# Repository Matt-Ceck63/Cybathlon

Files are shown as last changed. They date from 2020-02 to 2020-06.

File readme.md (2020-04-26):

This repository contains:

- Main assembly in solidworks (Old version, newer version saved in step files made in Fusion 360)
- Step Files:
	- Arm Assembly
	- Manipulator Assembly
- Bill of materials
- STM32F303K8 microcontroller reference files
- C program for the microcontroller
- Whole Cybathlon team wheelchair assembly with mounted arm

Rendered Assembly:

Front Side

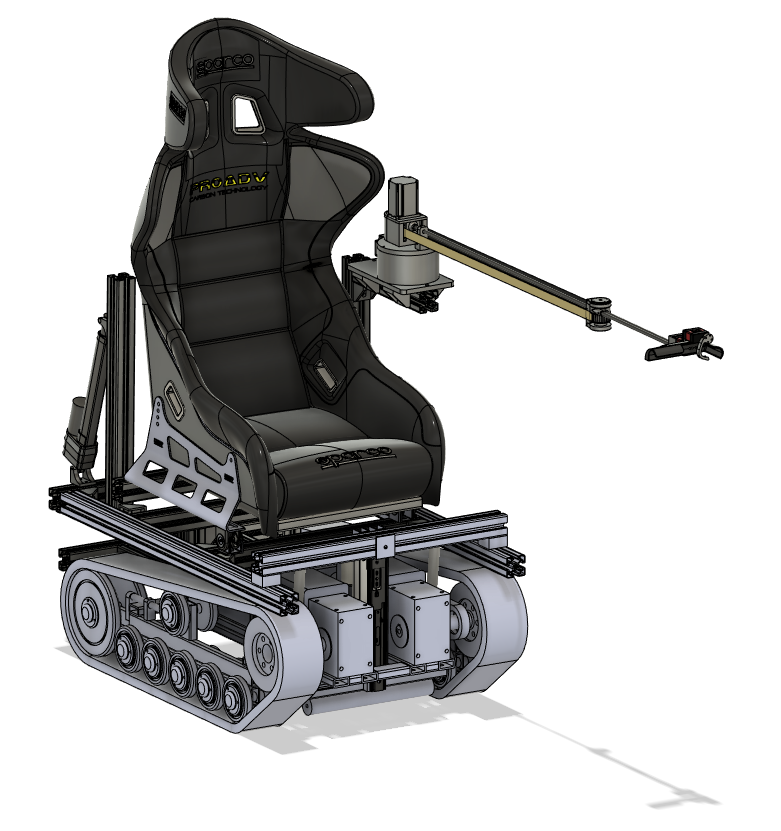
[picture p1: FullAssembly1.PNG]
Image Front Side


Back Side

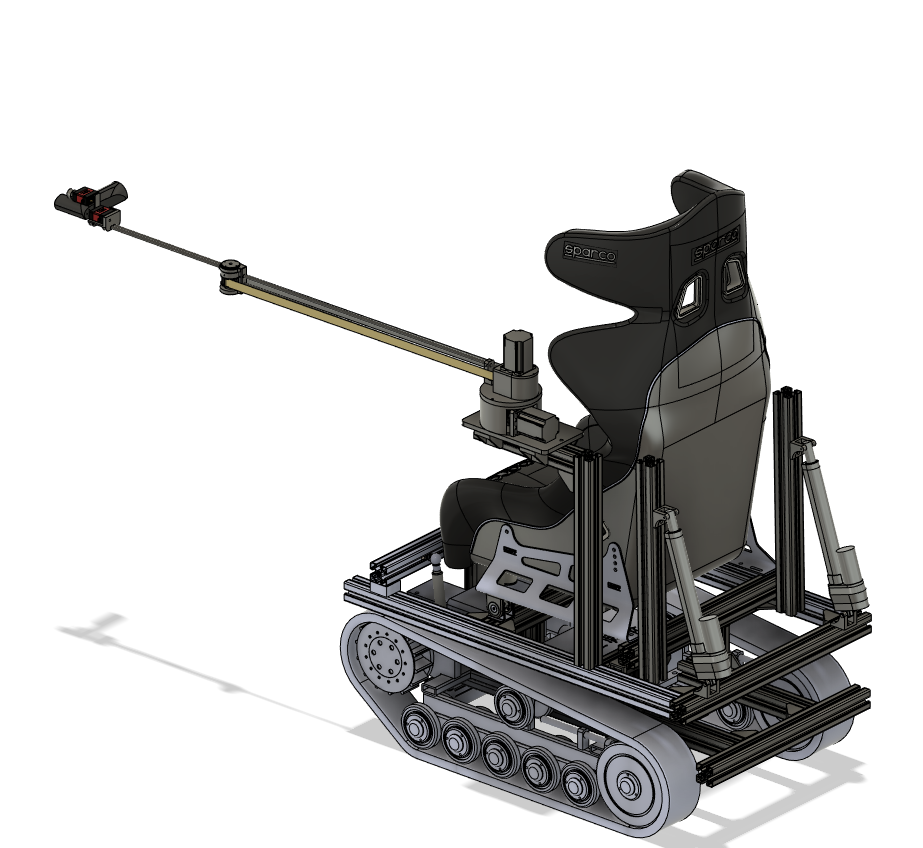
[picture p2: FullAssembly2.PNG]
Image Back Side


Top

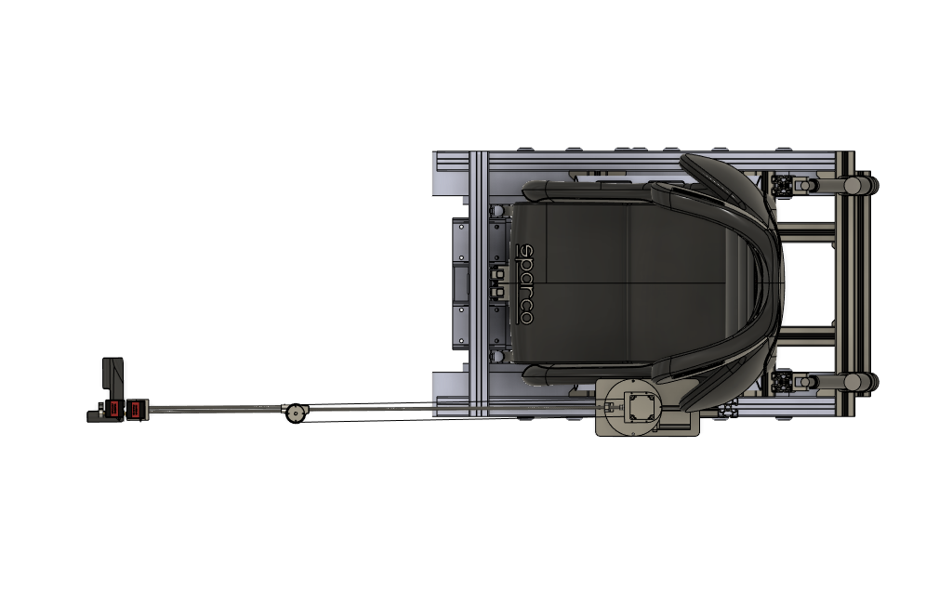
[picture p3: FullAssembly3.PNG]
Image Top


Front

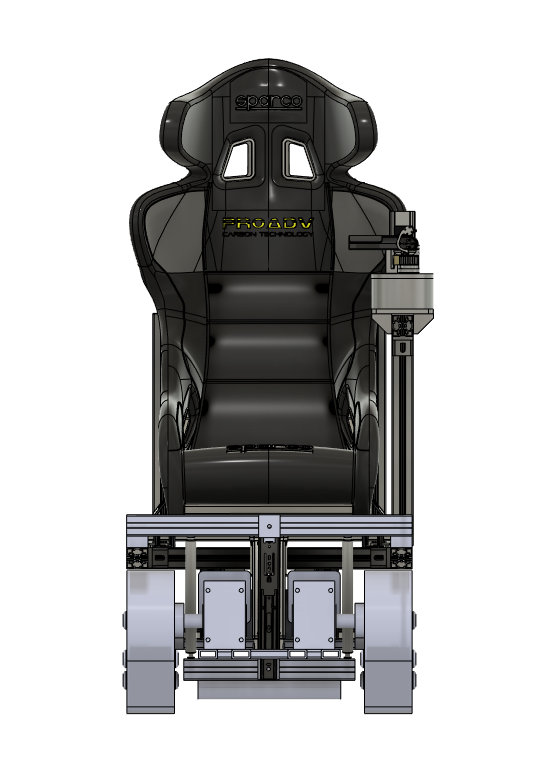
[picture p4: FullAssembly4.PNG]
Image Front


Retracted Arm

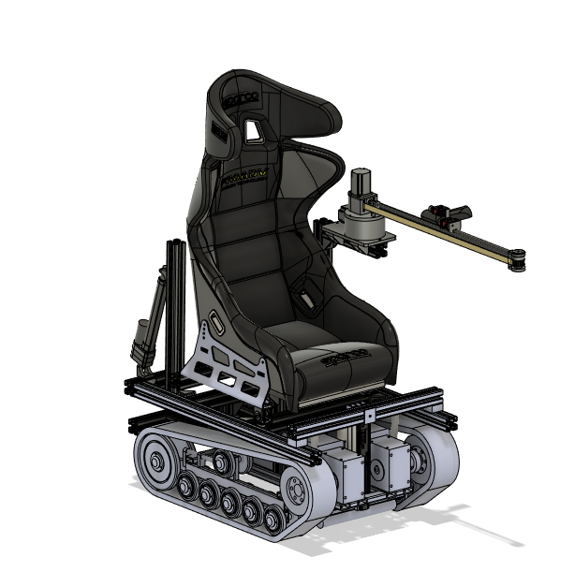
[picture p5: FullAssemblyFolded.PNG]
Image Retracted Arm


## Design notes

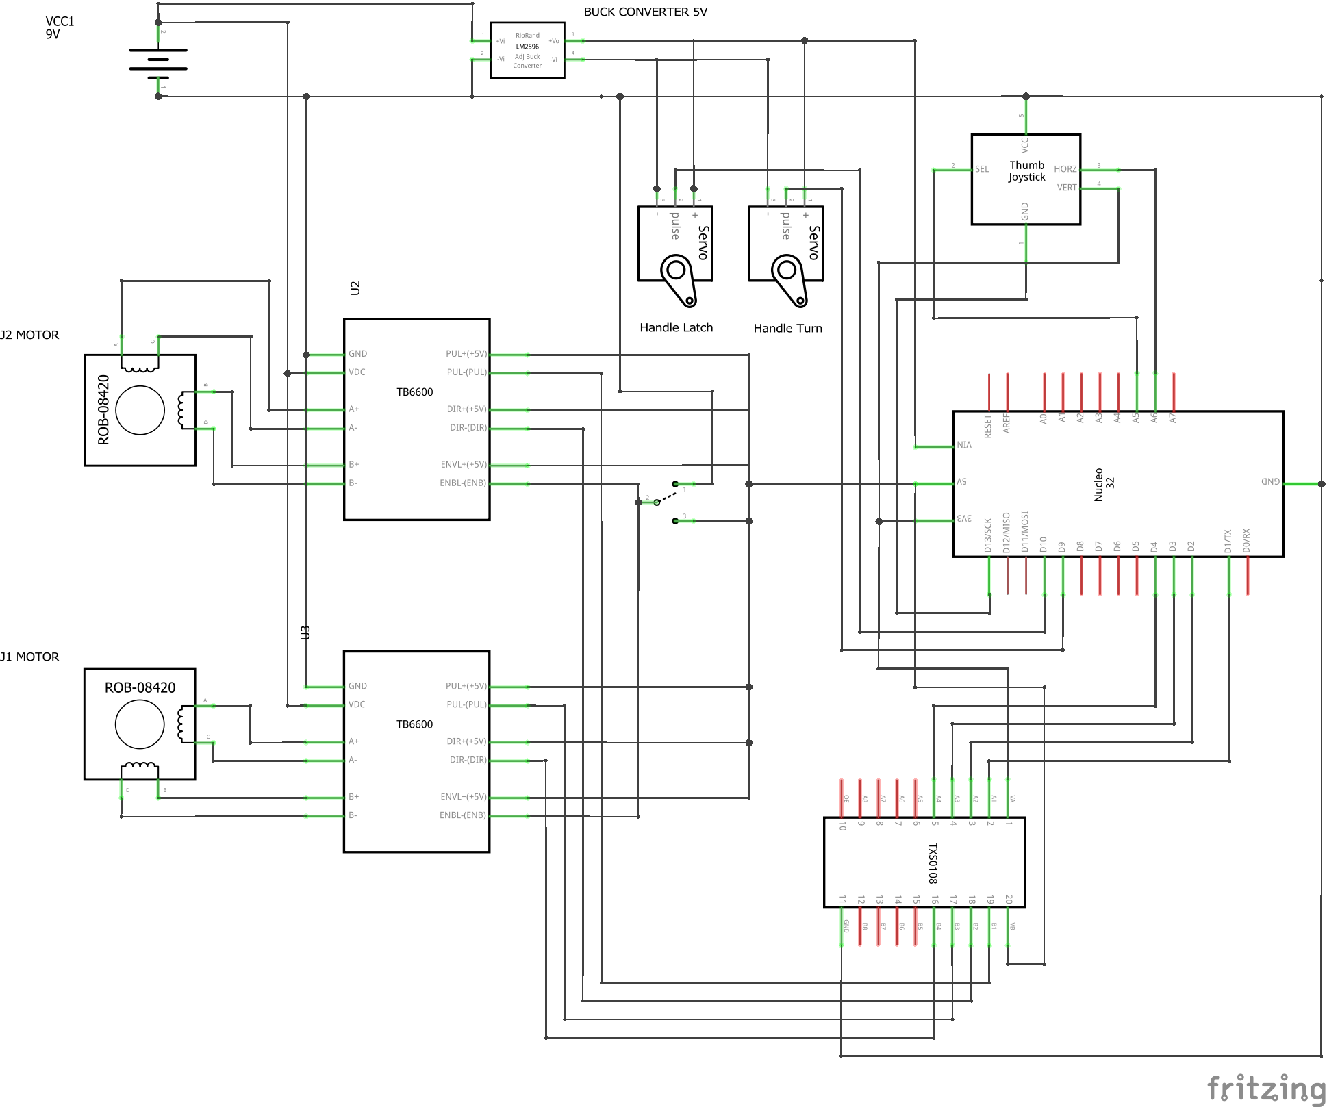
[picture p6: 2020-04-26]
Electronics/Schematic.png

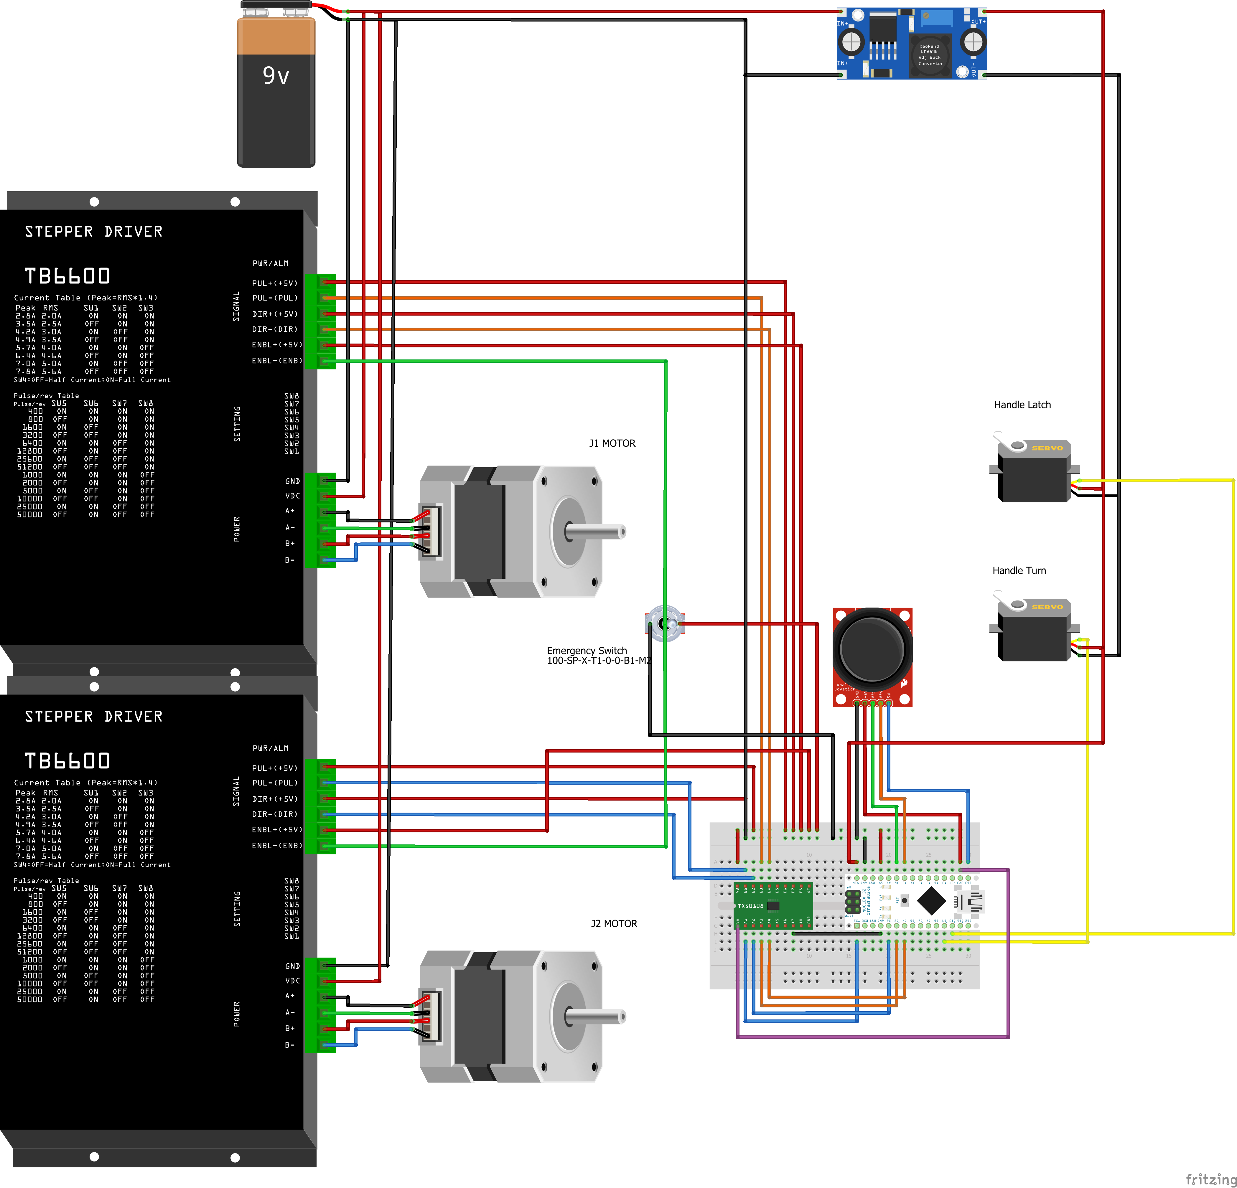
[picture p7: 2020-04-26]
Electronics/Breadboard.png

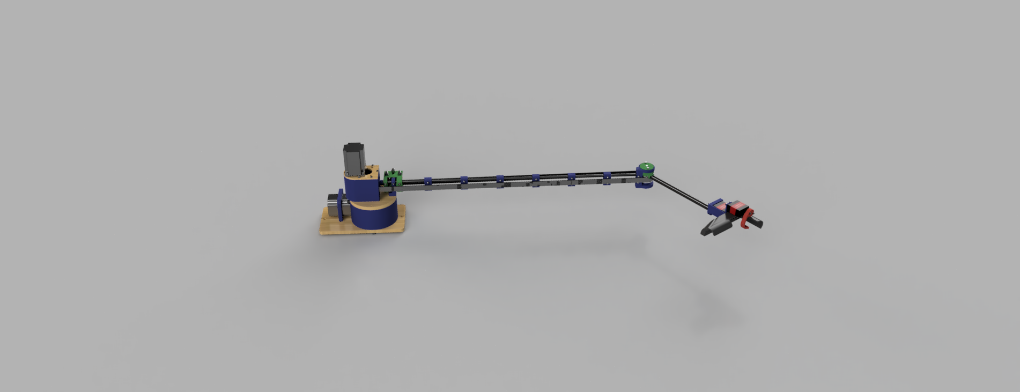
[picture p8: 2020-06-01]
Renders/721365d3-7628-4a67-89fb-87a22e6670c4.PNG

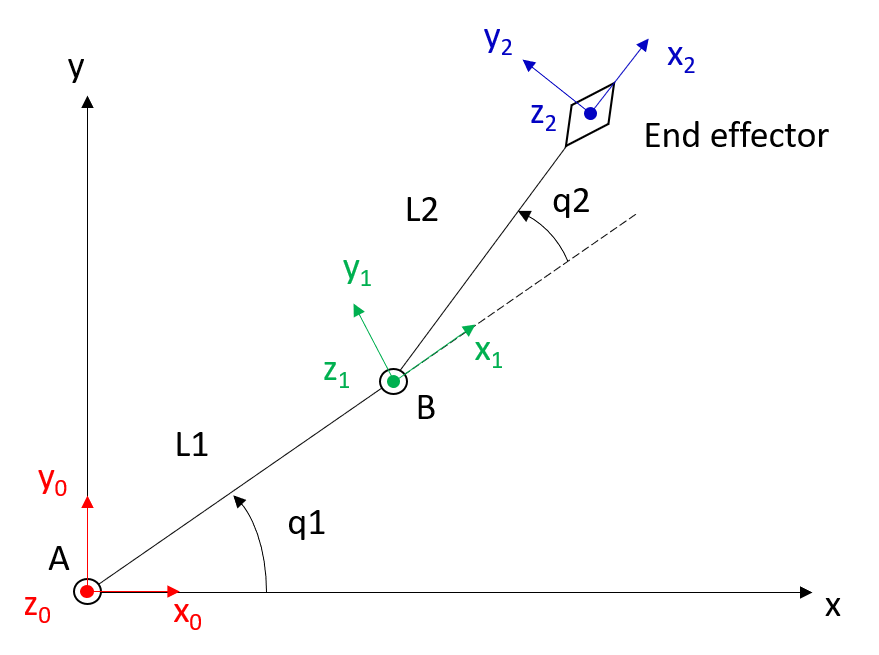
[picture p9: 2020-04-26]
Drawings/Picture2.png

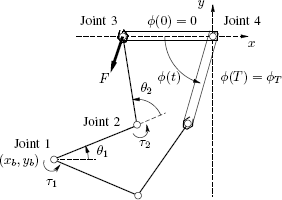
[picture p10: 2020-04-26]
Drawings/5354076-fig-1-source-small.gif

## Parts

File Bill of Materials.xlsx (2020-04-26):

BILL OF MATERIALS
Item | Details | Amount | Code | Cost | Datasheet link | Link | Unit Price
Bearings |  |  |  |  |  | https://uk.rs-online.com/web/p/roller-bearings/2868369/ | 19.96
Taper Roller Bearing | 15x42mm | 1 | RS-286-8369 | £19.96 |  | https://uk.rs-online.com/web/p/ball-bearings/6189913/ | 2.1
Ball Bearing | 6x19x6mm | 5 | RS-618-9913 | £10.50 |  | https://www.amazon.co.uk/gp/product/B078R9JJDY/ref=ppx_yo_dt_b_asin_title_o01_s00?ie=UTF8&psc=1
Flanged bearings | 6x13x5mm | 6 |  | £5.99
Shafts and rods
Aluminium shaft | 6mmx1m | 1 |  | N/A |  |  | 9.5
Hollow carbon fiber tube | 8mmx1m | 2 |  | £19.00
Motor Shaft mounting hub | 6mm | 1 |  | £6.00
Flexible shaft coupler | ID6.35x6xOD19xL25mm | 2 |  | £7.55
Transmission |  |  |  |  | https://khkgears2.net/catalog5/AG1-30R1 | https://uk.rs-online.com/web/p/worm-wheel-gears/5216957/ | 34.22
Worm Wheel | 30 teeth | 1 | RS-521-6957 | £34.22 | https://khkgears2.net/catalog5/SWG1-R1 | https://uk.rs-online.com/web/p/worm-gears/5216890/ | 13.99
Worm Gear | 32 mm | 1 | RS-521-521-6890 | £13.99
Timing belt | 1500 mm loop | 1 |  | £14.27 |  |  | 10.31
Belt pulley |  | 2 |  | £20.62
Electronics |  |  |  |  |  |  | 50
Stepper motor | 2 Nm Nema23 57*57*76mm | 2 |  | £100.00 |  | https://www.amazon.co.uk/dp/B07CMBMWZW | 20
Servo motor | 20 Kg*cm | 2 | LD-220MG | £40.00
Nucleo 32 |  | 1 | NUCLEO-F303K8 | £10.22 |  | https://www.amazon.co.uk/Quimat-Upgraded-Version-Segments-Stepper/dp/B06XSBB45M?s=industrial | 13.99
Stepper motor driver | TB6600 | 2 | Quimat TB6600 | £27.98 |  | https://www.amazon.co.uk/gp/slredirect/picassoRedirect.html?adId=A02853972WMKXGN6MCET5&qualifier=1587392253&id=8120630561316040&widgetName=sp_atf
Dc buck converter | LM2596 | 1 |  | £8.99
Logic level converter |  | 1 | TX50108E | £5.99
Electric Switch |  | 1 |  | N/A
Joystick |  | 1 |  | N/A
Structural materials
PLA |  | 500 g |  | £18.00
MDF | 250x250x5mm | 1 |  | £50.00
Fasteners
M3x10mm Bolt |  | 12 |  | N/A
M3x20mm Bolt |  | 25 |  | N/A
M3x22mm Bolt |  | 27 |  | N/A
M3x30mm Bolt |  | 2 |  | N/A
M3 Nut |  | 43 |  | N/A
M5x20mm Bolt |  | 12 |  | N/A
M5 Nut |  | 4 |  | N/A
M6x30mm Bolt |  | 3 |  | N/A
M6x50mm Bolt |  | 3 |  | N/A
M6 Nut |  | 28 |  | N/A
M6 Washer |  | 8 |  | N/A
 |  |  | Total | £413.28

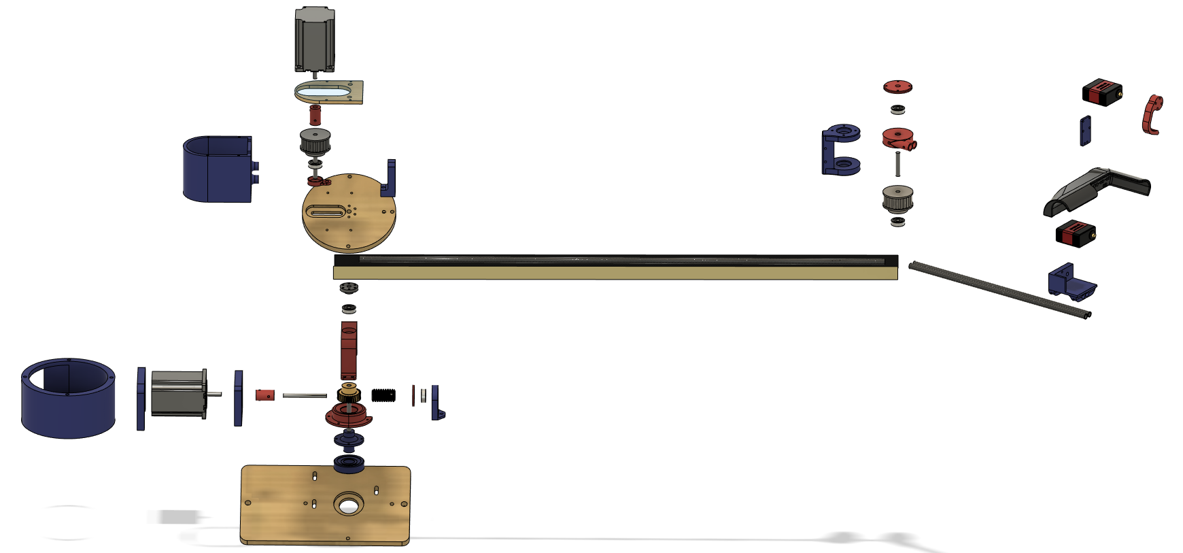
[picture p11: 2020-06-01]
Renders/Arm Components Description.PNG

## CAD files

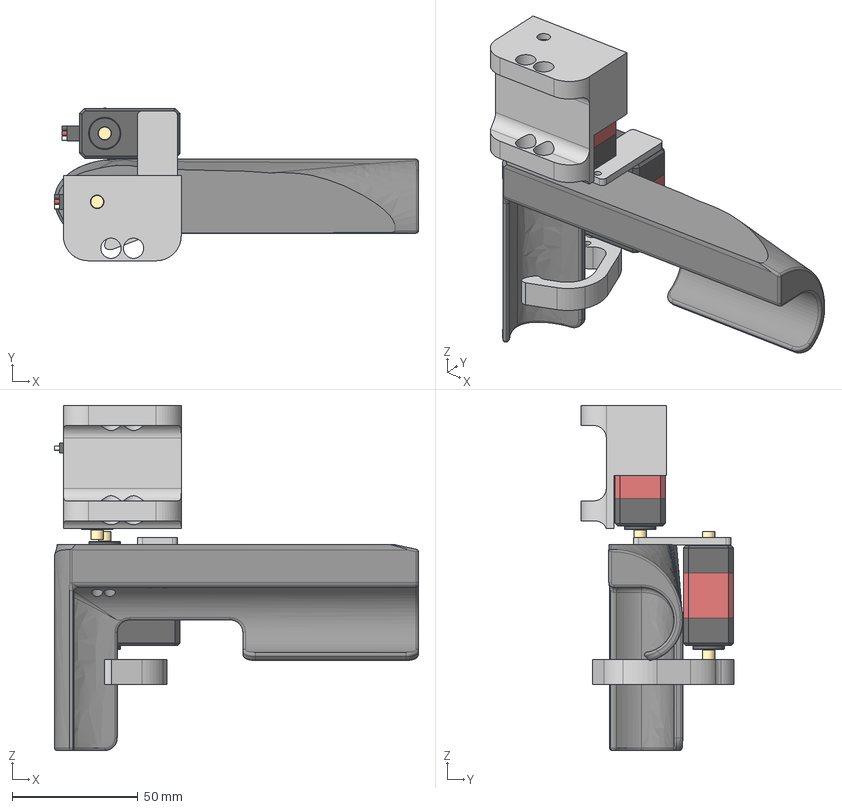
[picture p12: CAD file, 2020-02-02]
Step files/Handle assembly.step
145.0 x 60.8 x 137.5 mm
LD-220MG Servo x 2
Handle Lock
HandleOpener Final
Lock Servo Bracket
Manipulator Base

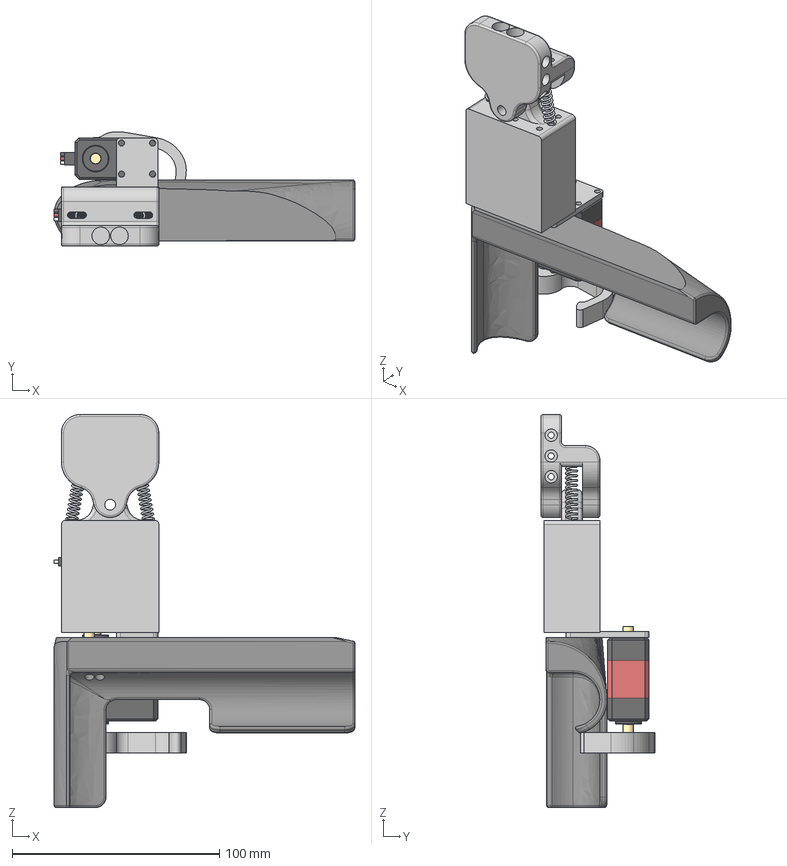
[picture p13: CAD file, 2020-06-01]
CAD files/End Effector.step
145.0 x 55.2 x 189.5 mm
LD-220MG Servo x 2
HandleOpener Final
Handle Lock
Lock Servo Bracket
Manipulator Base
Spring
Link Mount
Spring(Mirror)

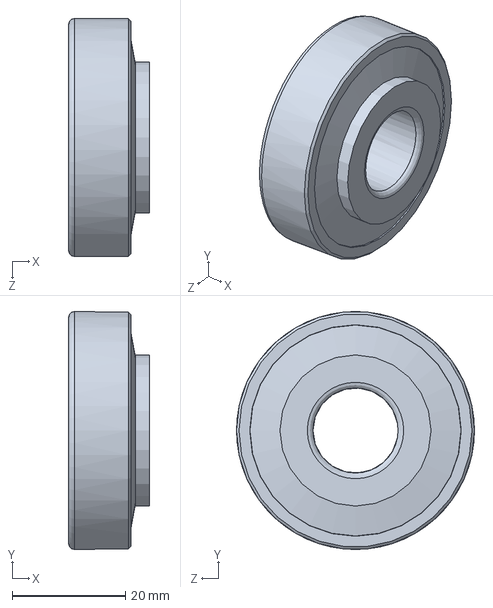
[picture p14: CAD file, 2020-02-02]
Main Arm Assembly/Bearings/Taper Roller Bearing 30302-J2.SLDPRT
14.2 x 42.0 x 42.0 mm

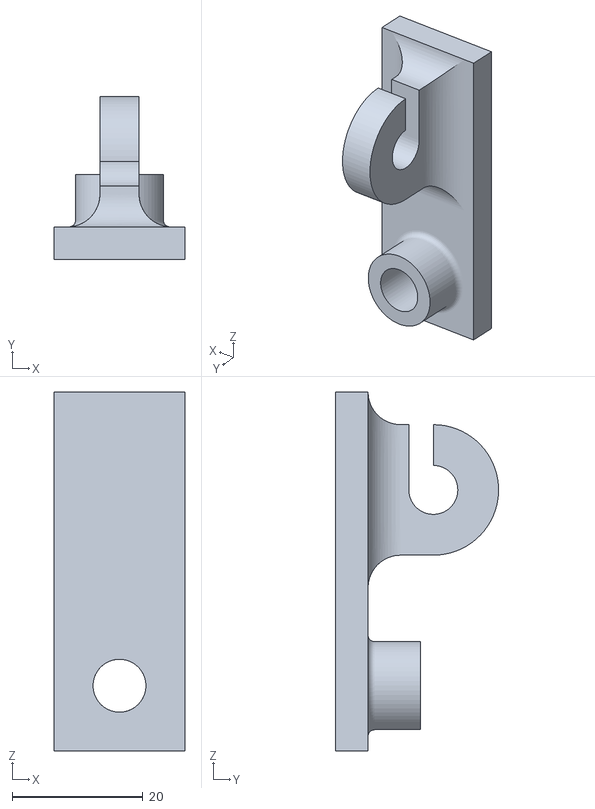
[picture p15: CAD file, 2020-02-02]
Main Arm Assembly/Handle Opening/Profile hook bottom v3.stl
20.0 x 25.0 x 55.0

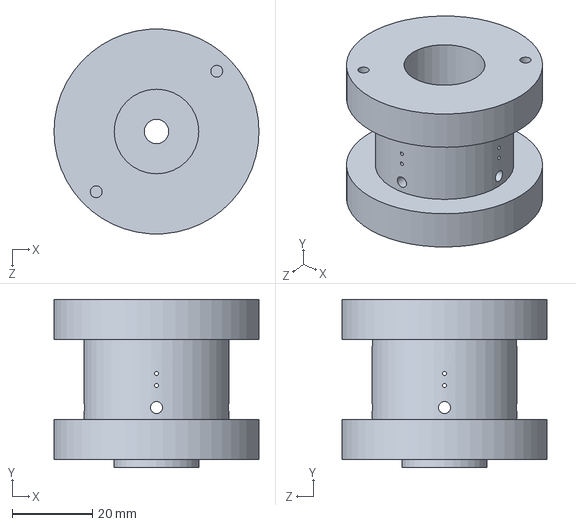
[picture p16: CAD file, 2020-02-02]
Main Arm Assembly/Spool.SLDPRT
51.1 x 42.0 x 51.0 mm

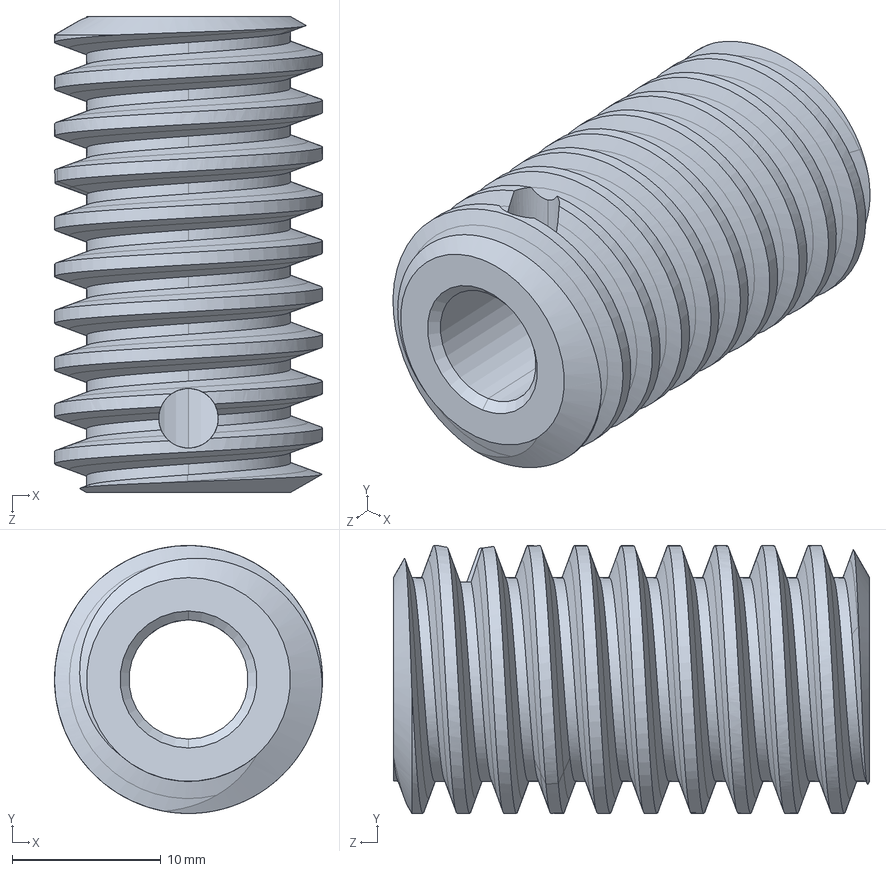
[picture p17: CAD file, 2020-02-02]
Main Arm Assembly/Transmission/KHK_US-SWG1-R1.SLDPRT
18.0 x 18.0 x 32.0 mm

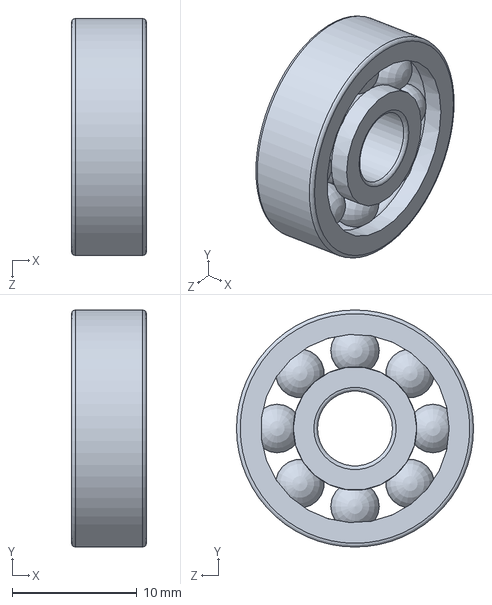
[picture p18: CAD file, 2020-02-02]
Main Arm Assembly/Bearings/RS-618-9913.SLDPRT
6.00 x 19.0 x 19.0 mm

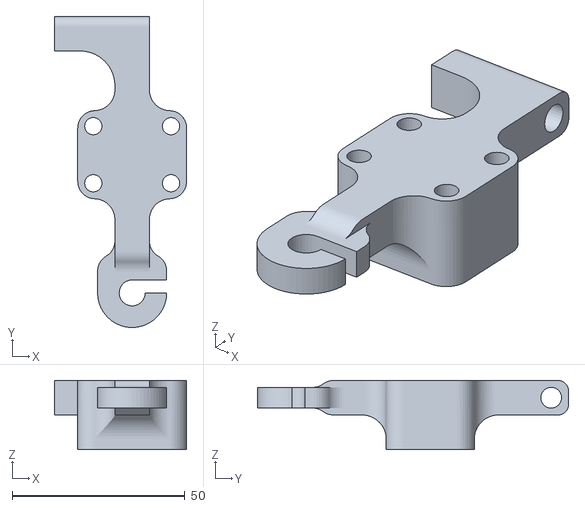
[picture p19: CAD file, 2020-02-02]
Main Arm Assembly/Handle Opening/Motor Hook v8.stl
38.2 x 90.0 x 20.0

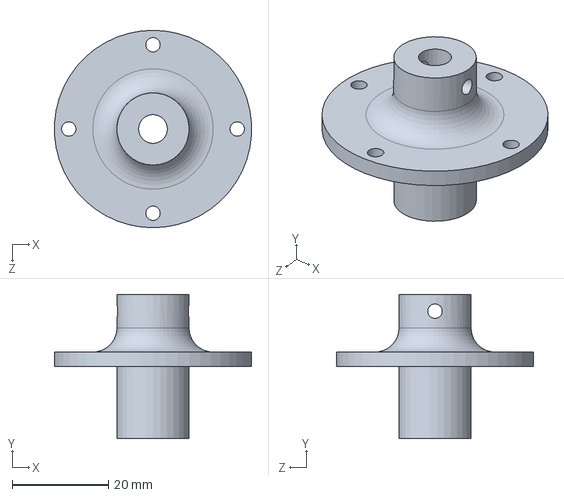
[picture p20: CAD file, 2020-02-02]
Main Arm Assembly/shaft-tapered coupler.SLDPRT
40.9 x 30.0 x 41.0 mm

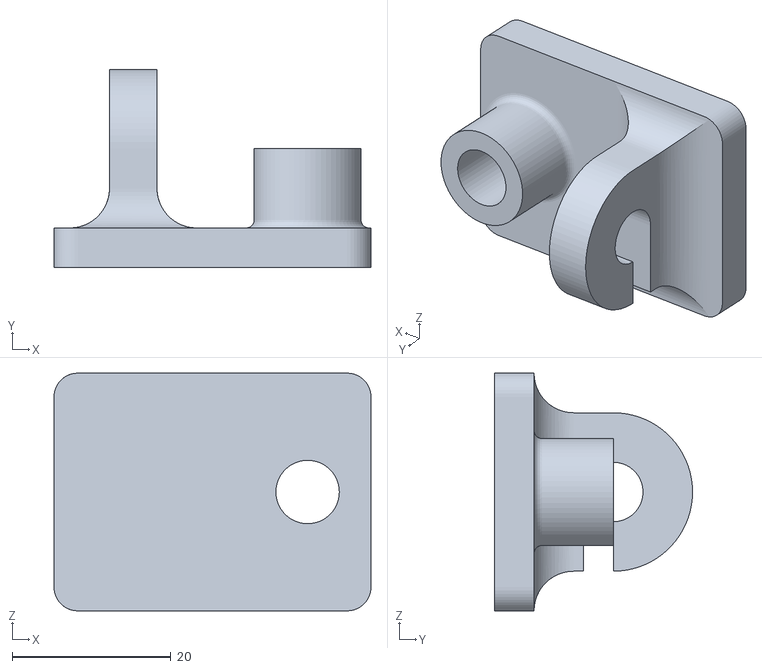
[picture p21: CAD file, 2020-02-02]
Main Arm Assembly/Handle Opening/Profile Hook Sideways v8.stl
40.0 x 25.0 x 30.0

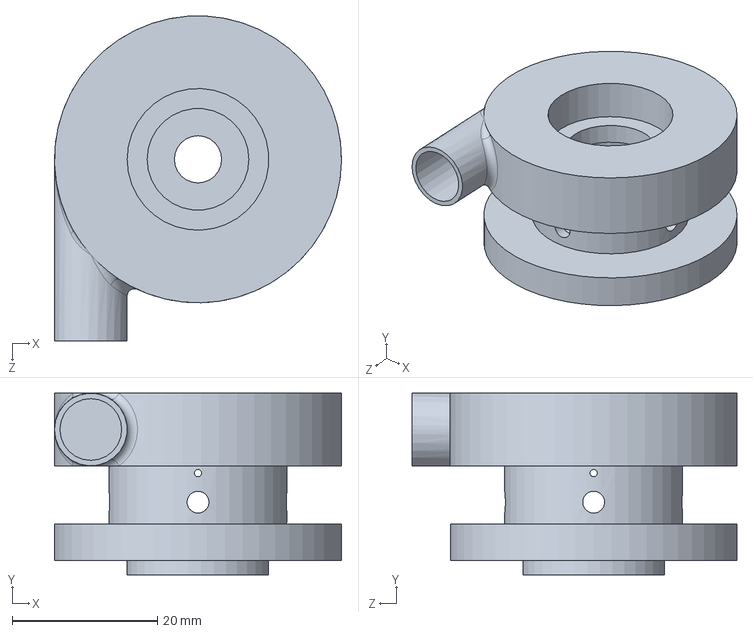
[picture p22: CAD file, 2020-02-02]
Main Arm Assembly/J2 Spool.SLDPRT
39.5 x 25.0 x 44.7 mm

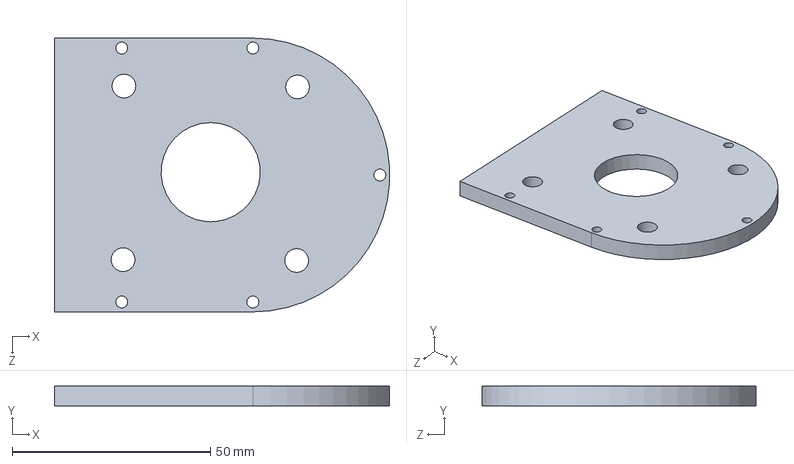
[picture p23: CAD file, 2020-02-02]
Main Arm Assembly/J2 Motor Mount v2.SLDPRT
84.4 x 5.00 x 69.0 mm

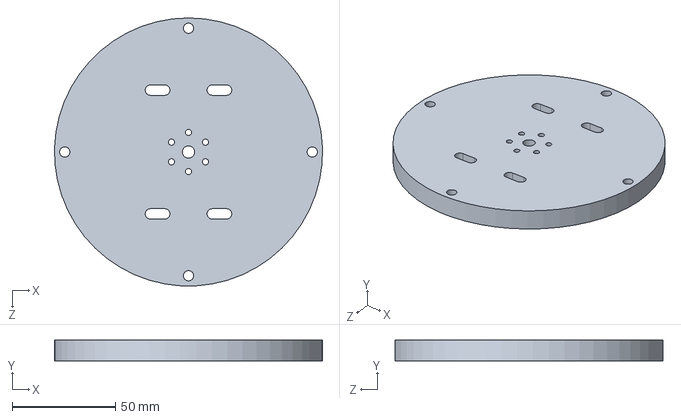
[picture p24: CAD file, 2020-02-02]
Main Arm Assembly/J2 Base.SLDPRT
129.9 x 10.0 x 130.0 mm

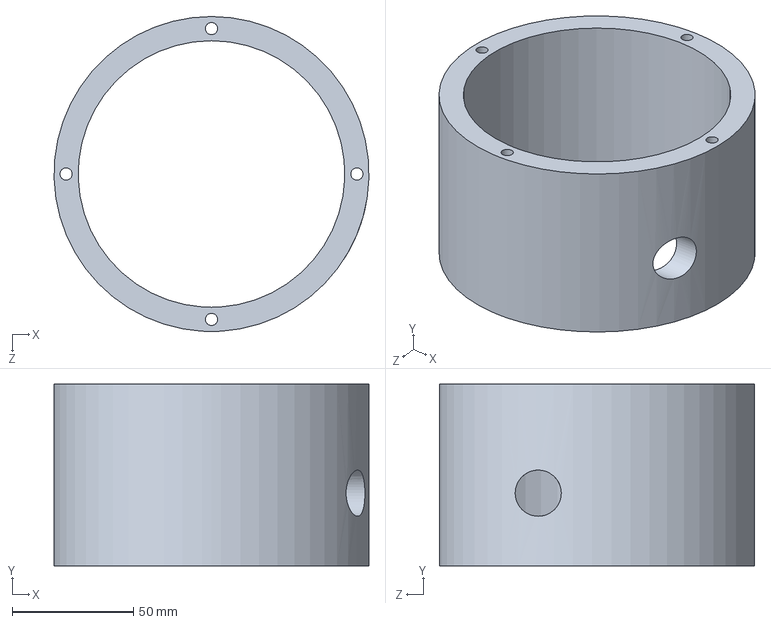
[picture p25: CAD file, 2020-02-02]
Main Arm Assembly/Joint 1 Casing.SLDPRT
129.9 x 75.0 x 130.0 mm

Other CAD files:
Main Arm Assembly/6mm shaft 3.SLDPRT
Main Arm Assembly/8mm CF tube.SLDPRT
Main Arm Assembly/6mm shaft 2.SLDPRT
Main Arm Assembly/Rod Holder.SLDPRT
CAD files/End Effector.f3z
Main Arm Assembly/6mm shaft 1.SLDPRT
Main Arm Assembly/6mm shaft 4.SLDPRT
Main Arm Assembly/8mm CF tube 500 mm.SLDPRT
Main Arm Assembly/Base.SLDPRT
Main Arm Assembly/J1 Shaft Coupler.SLDPRT
Main Arm Assembly/J2 Motor Riser.SLDPRT
Main Arm Assembly/J2 Top Holder.SLDPRT
Main Arm Assembly/KHK_US-AG1-30R1.SLDPRT
Main Arm Assembly/Motor Mount.SLDPRT
Main Arm Assembly/Motor mounting hub M3 6mm shaft.step.SLDPRT
Main Arm Assembly/Spool Attachement.SLDPRT
Main Arm Assembly/Worm Gear Holder.SLDPRT
Main Arm Assembly/Worm Gear Shaft Bearing Tension ring.SLDPRT

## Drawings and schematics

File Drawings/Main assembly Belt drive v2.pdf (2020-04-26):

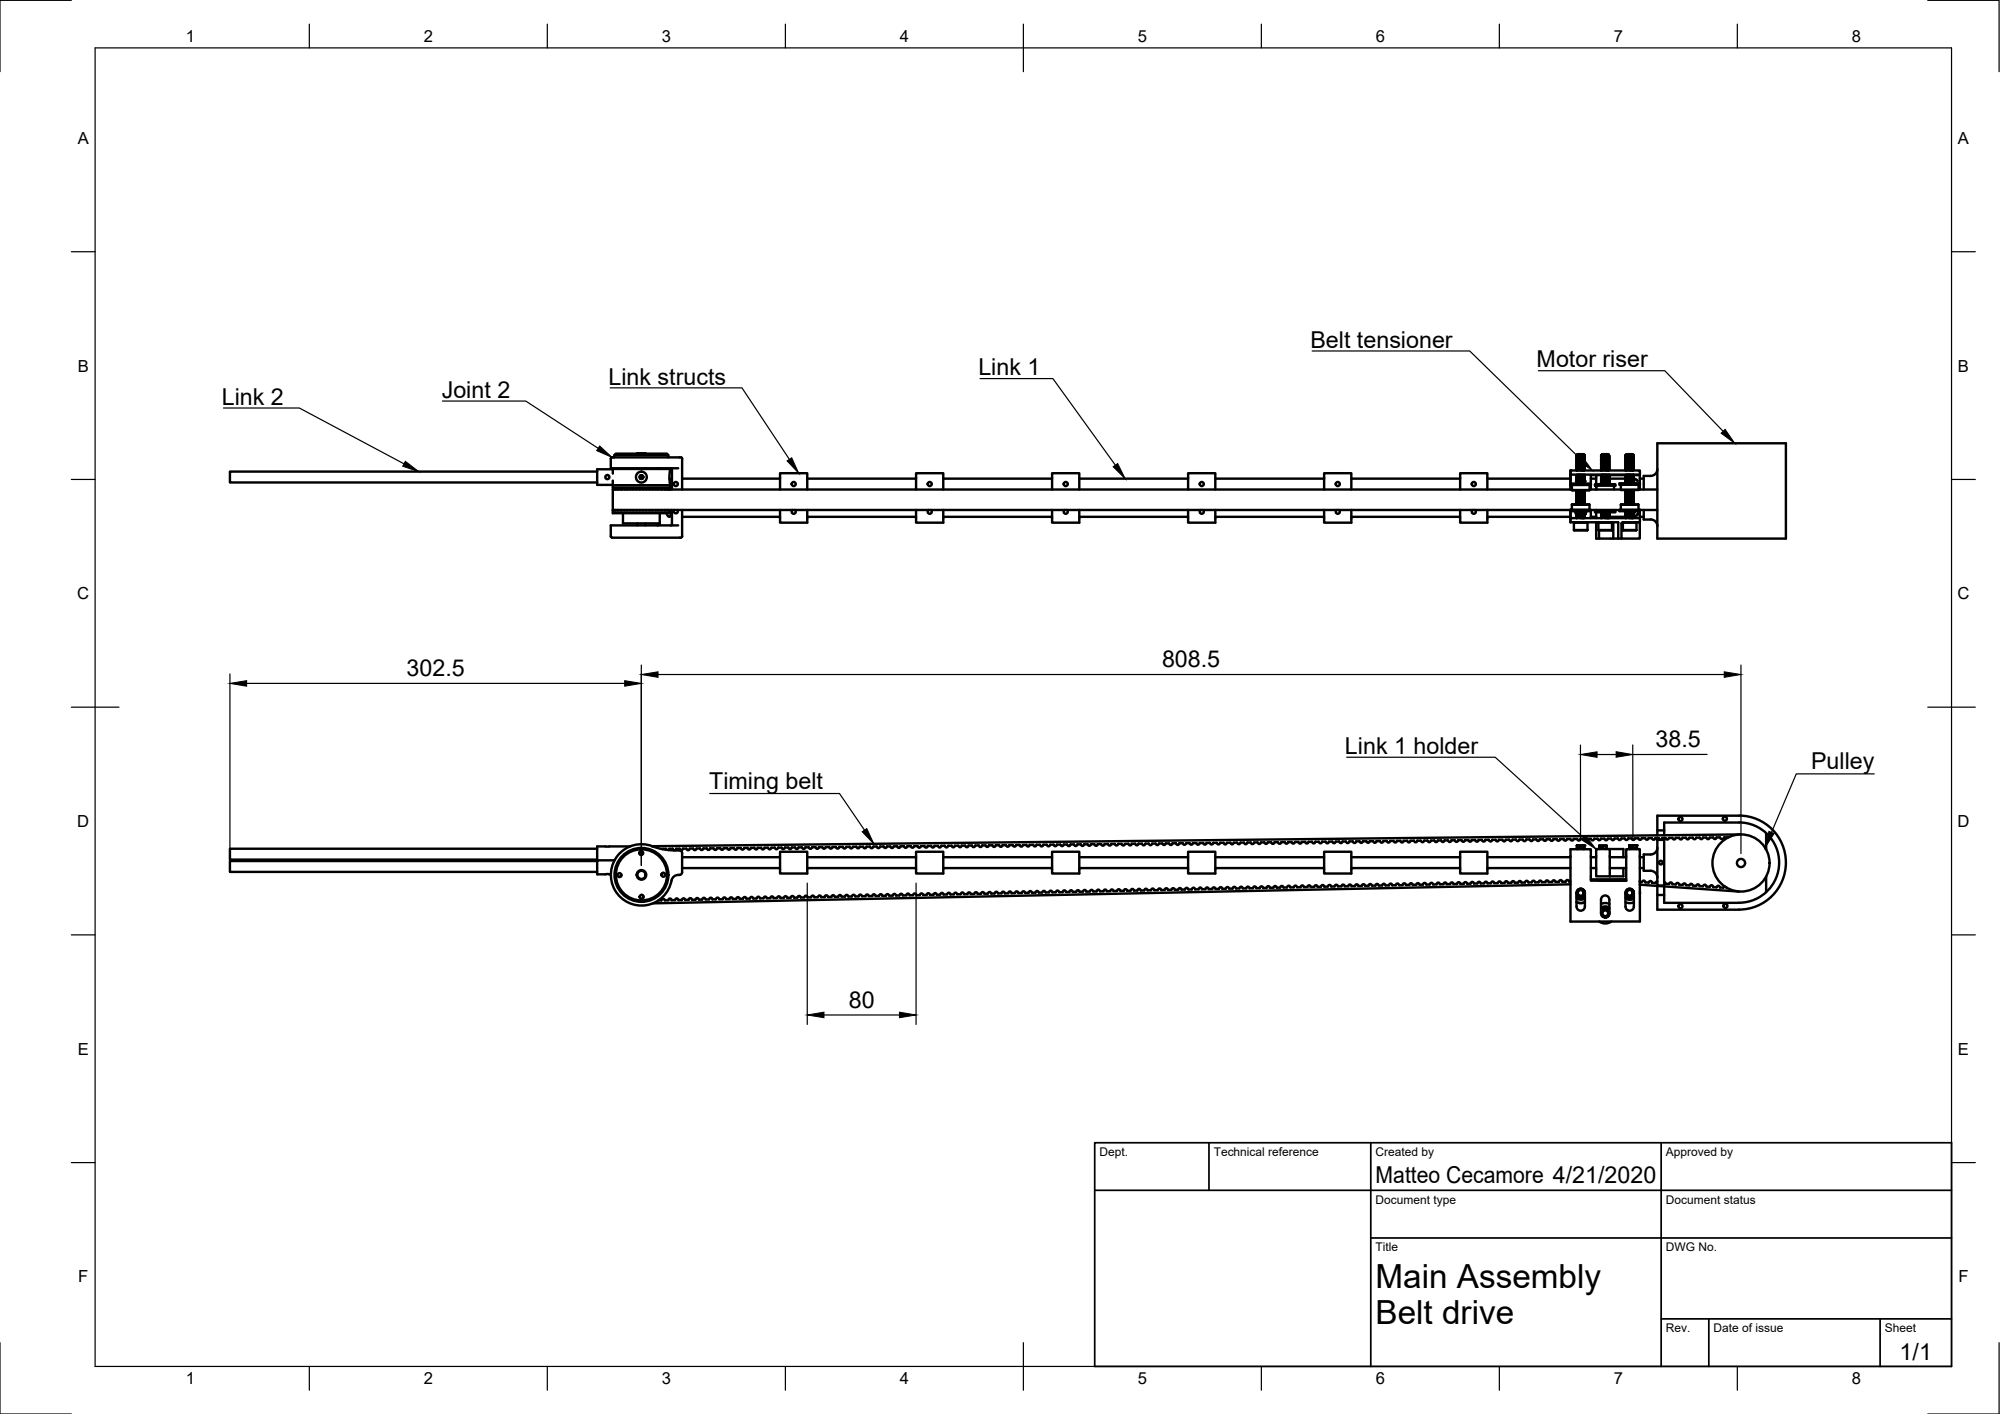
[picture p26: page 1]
Belt tensioner; Timing belt; Pulley; Link 1; Link 2; 38.5 Link 1 holder

Motor riser Link structs Joint 2

Dept. | Technical reference | Created by Matteo Cecamore 4/21/2020 | Approved by

Document type | Document status

Title Main Assembly Belt drive | DWG No.

Rev. | Date of issue | Sheet 1/1

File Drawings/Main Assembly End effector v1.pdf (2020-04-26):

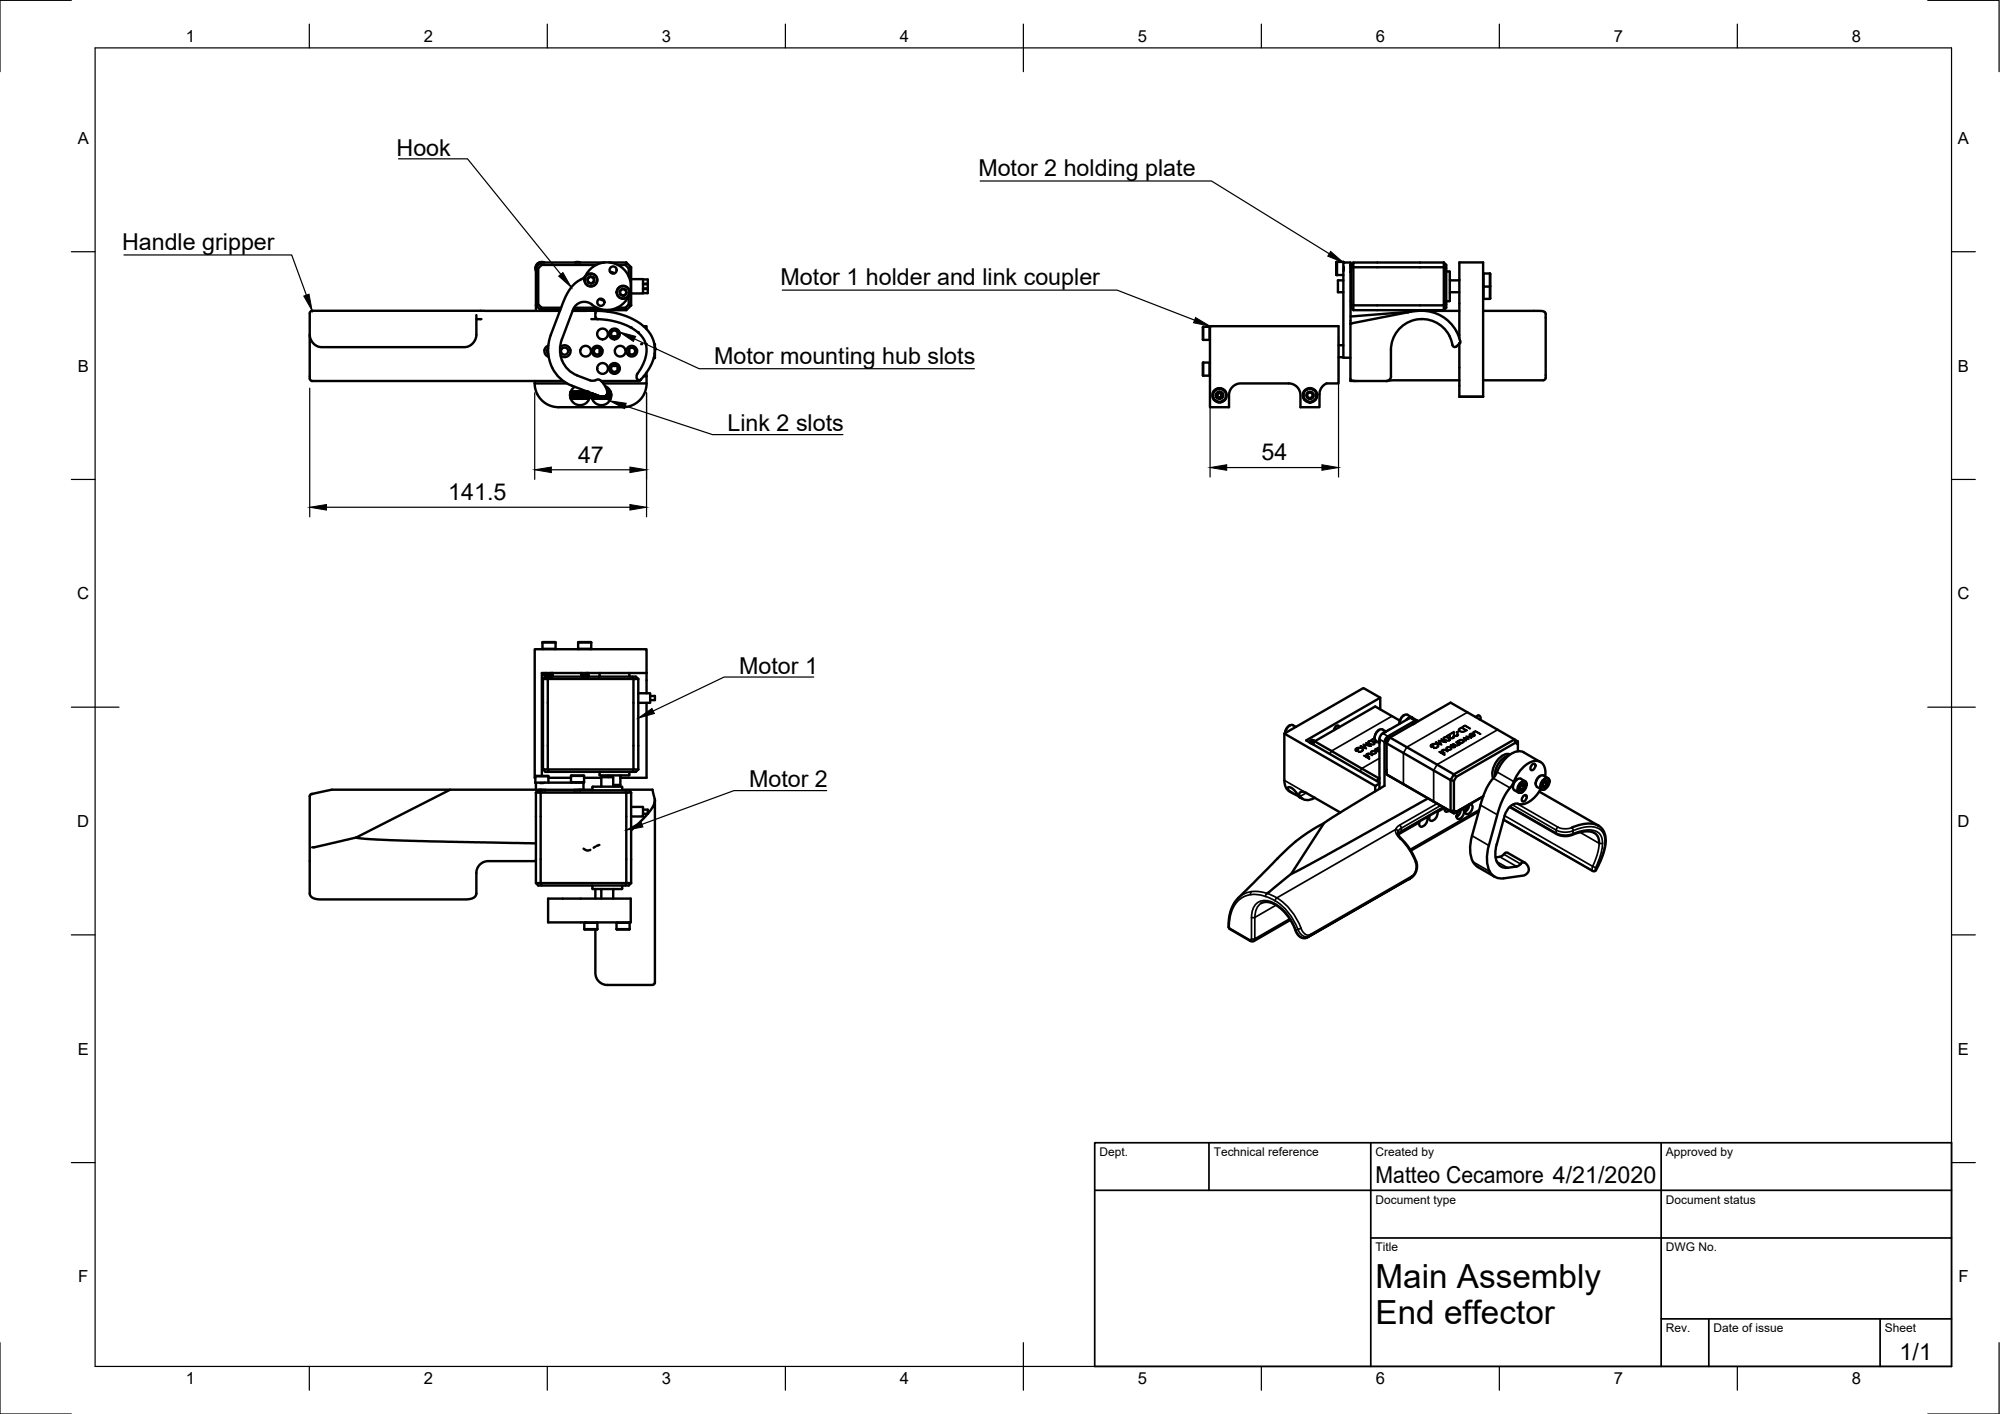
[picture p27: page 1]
Handle gripper; Link 2 slots; Motor 1; Motor 2

Motor 2 holding plate

Motor 1 holder and link coupler

Motor mounting hub slots

Dept. | Technical reference | Created by Matteo Cecamore 4/21/2020 | Approved by

Document type | Document status

Title Main Assembly End effector | DWG No.

Rev. | Date of issue | Sheet 1/1

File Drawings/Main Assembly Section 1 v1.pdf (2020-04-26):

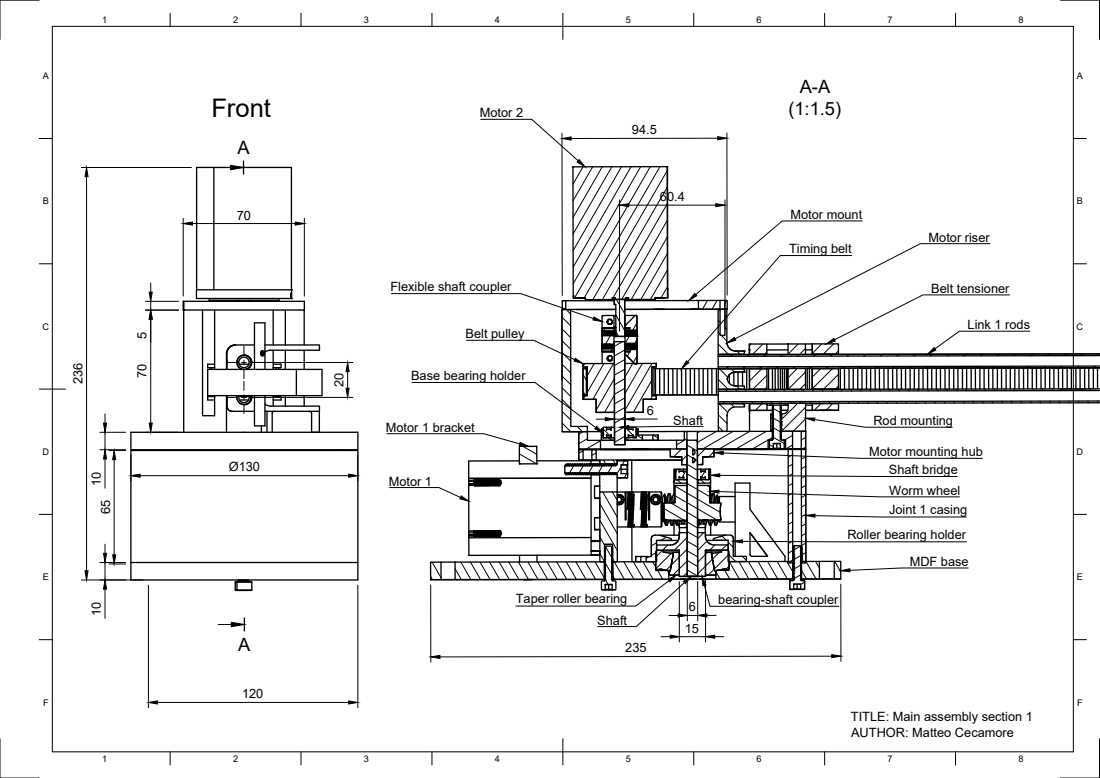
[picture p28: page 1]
Motor 2; Motor 1; Motor 1 bracket; Taper roller bearing; bearing-shaft coupler; MDF base; Timing belt; Belt tensioner; Link 1 rods; Rod mounting; Belt pulley; Motor mount; Motor riser; Front 236

Flexible shaft coupler

Base bearing holder

Motor mounting hub
Shaft bridge
Worm wheel
Joint 1 casing

Roller bearing holder

TITLE: Main assembly section 1
AUTHOR: Matteo Cecamore

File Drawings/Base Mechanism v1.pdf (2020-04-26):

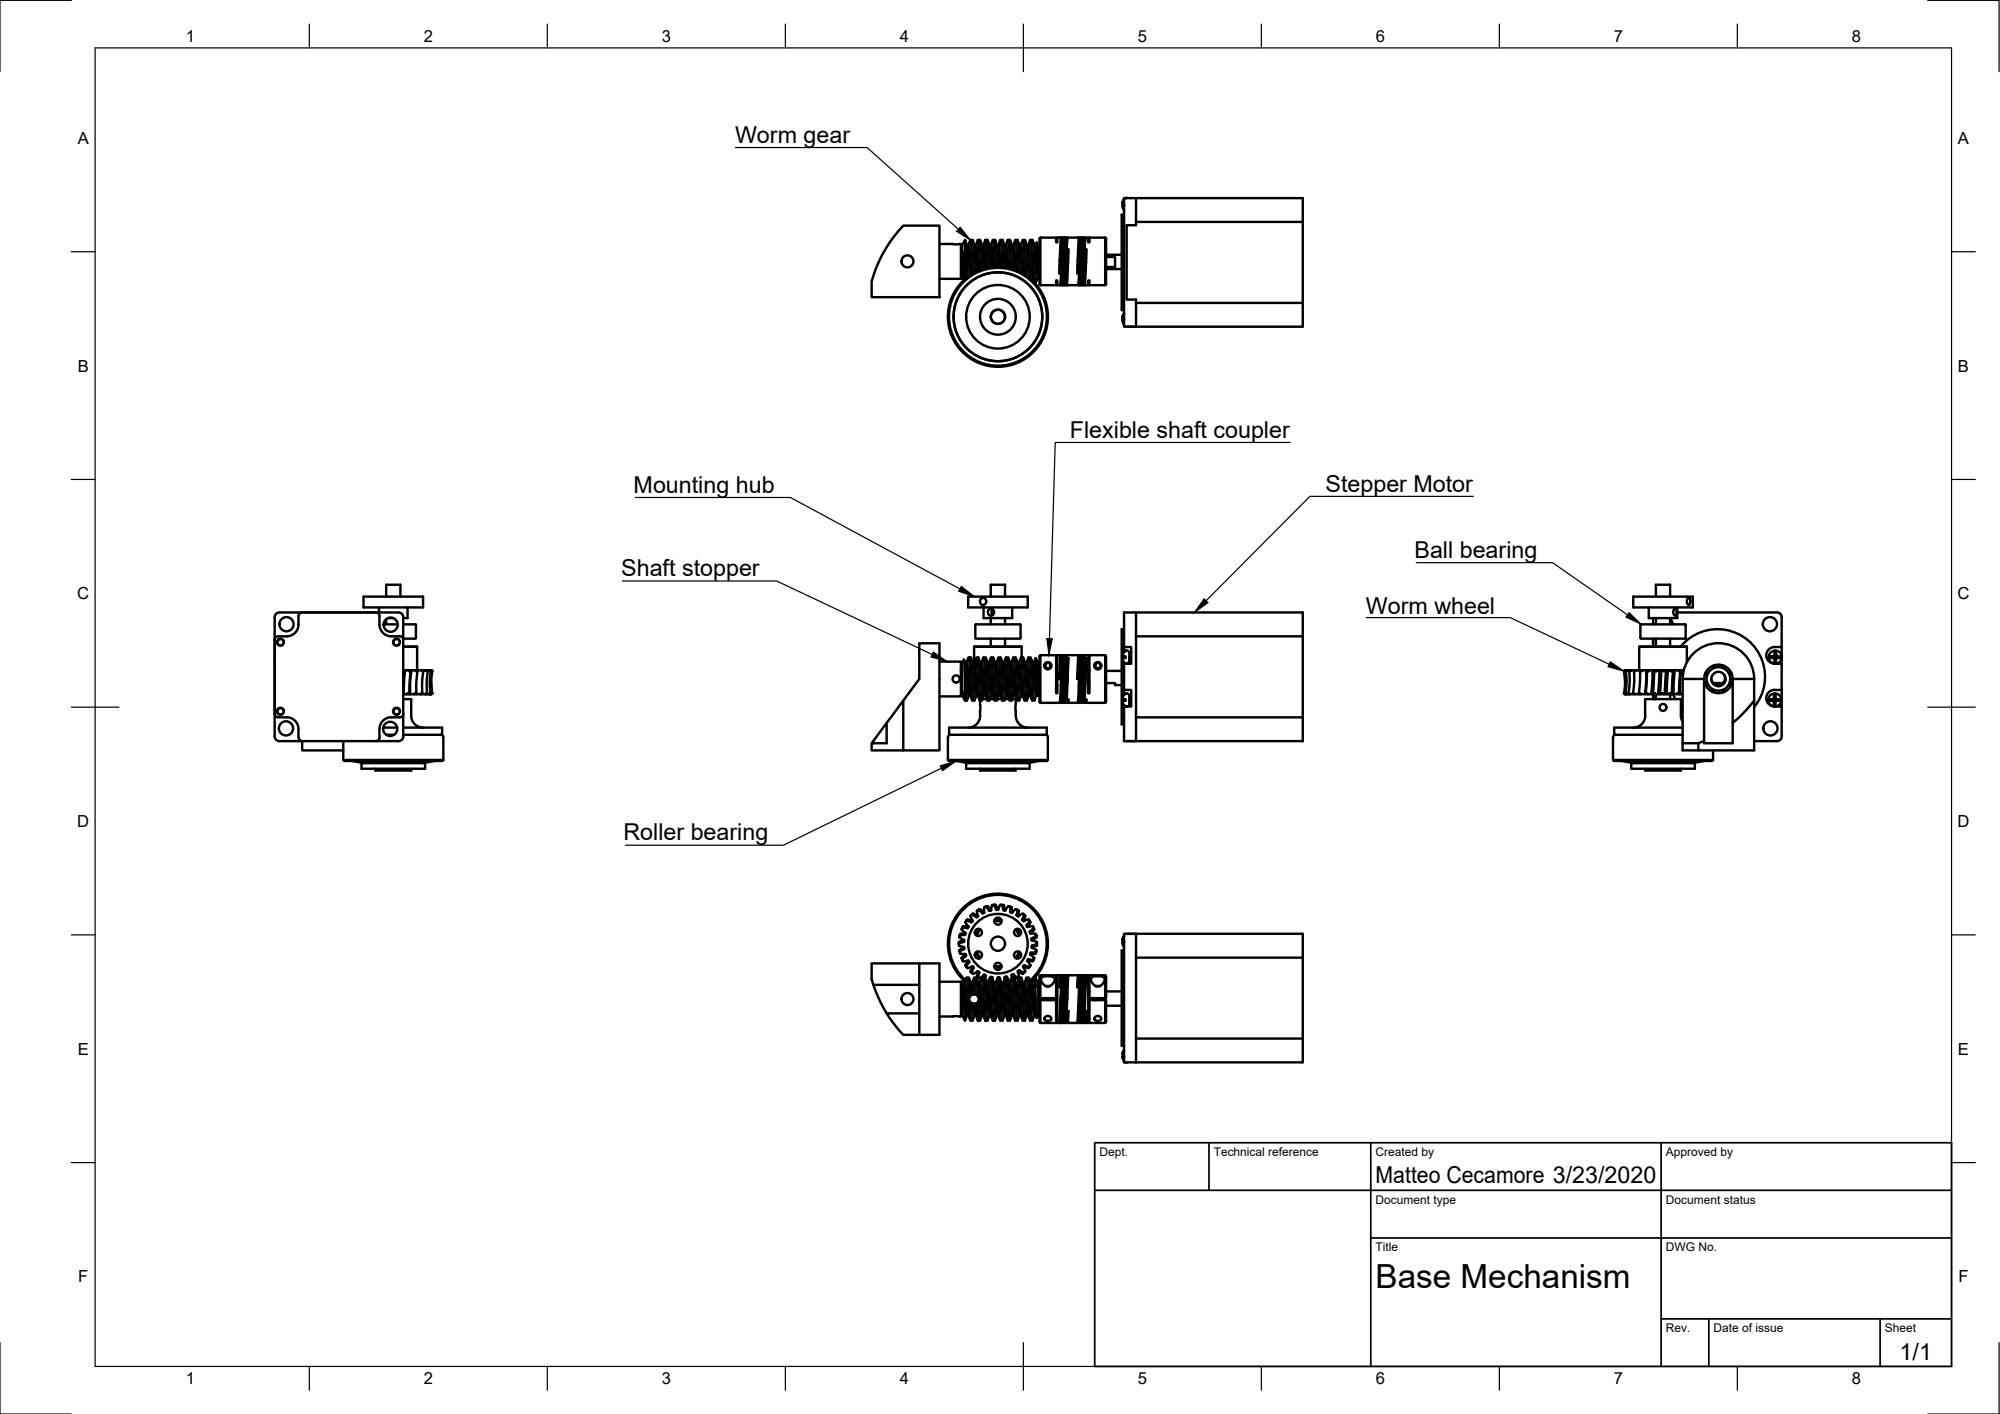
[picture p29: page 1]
Mounting hub; Stepper Motor; Roller bearing; Shaft stopper; Ball bearing; Worm wheel; Worm gear

Flexible shaft coupler

Dept. | Technical reference | Created by Matteo Cecamore 3/23/2020 | Approved by

Document type | Document status

Title Base Mechanism | DWG No.

Rev. | Date of issue | Sheet 1/1

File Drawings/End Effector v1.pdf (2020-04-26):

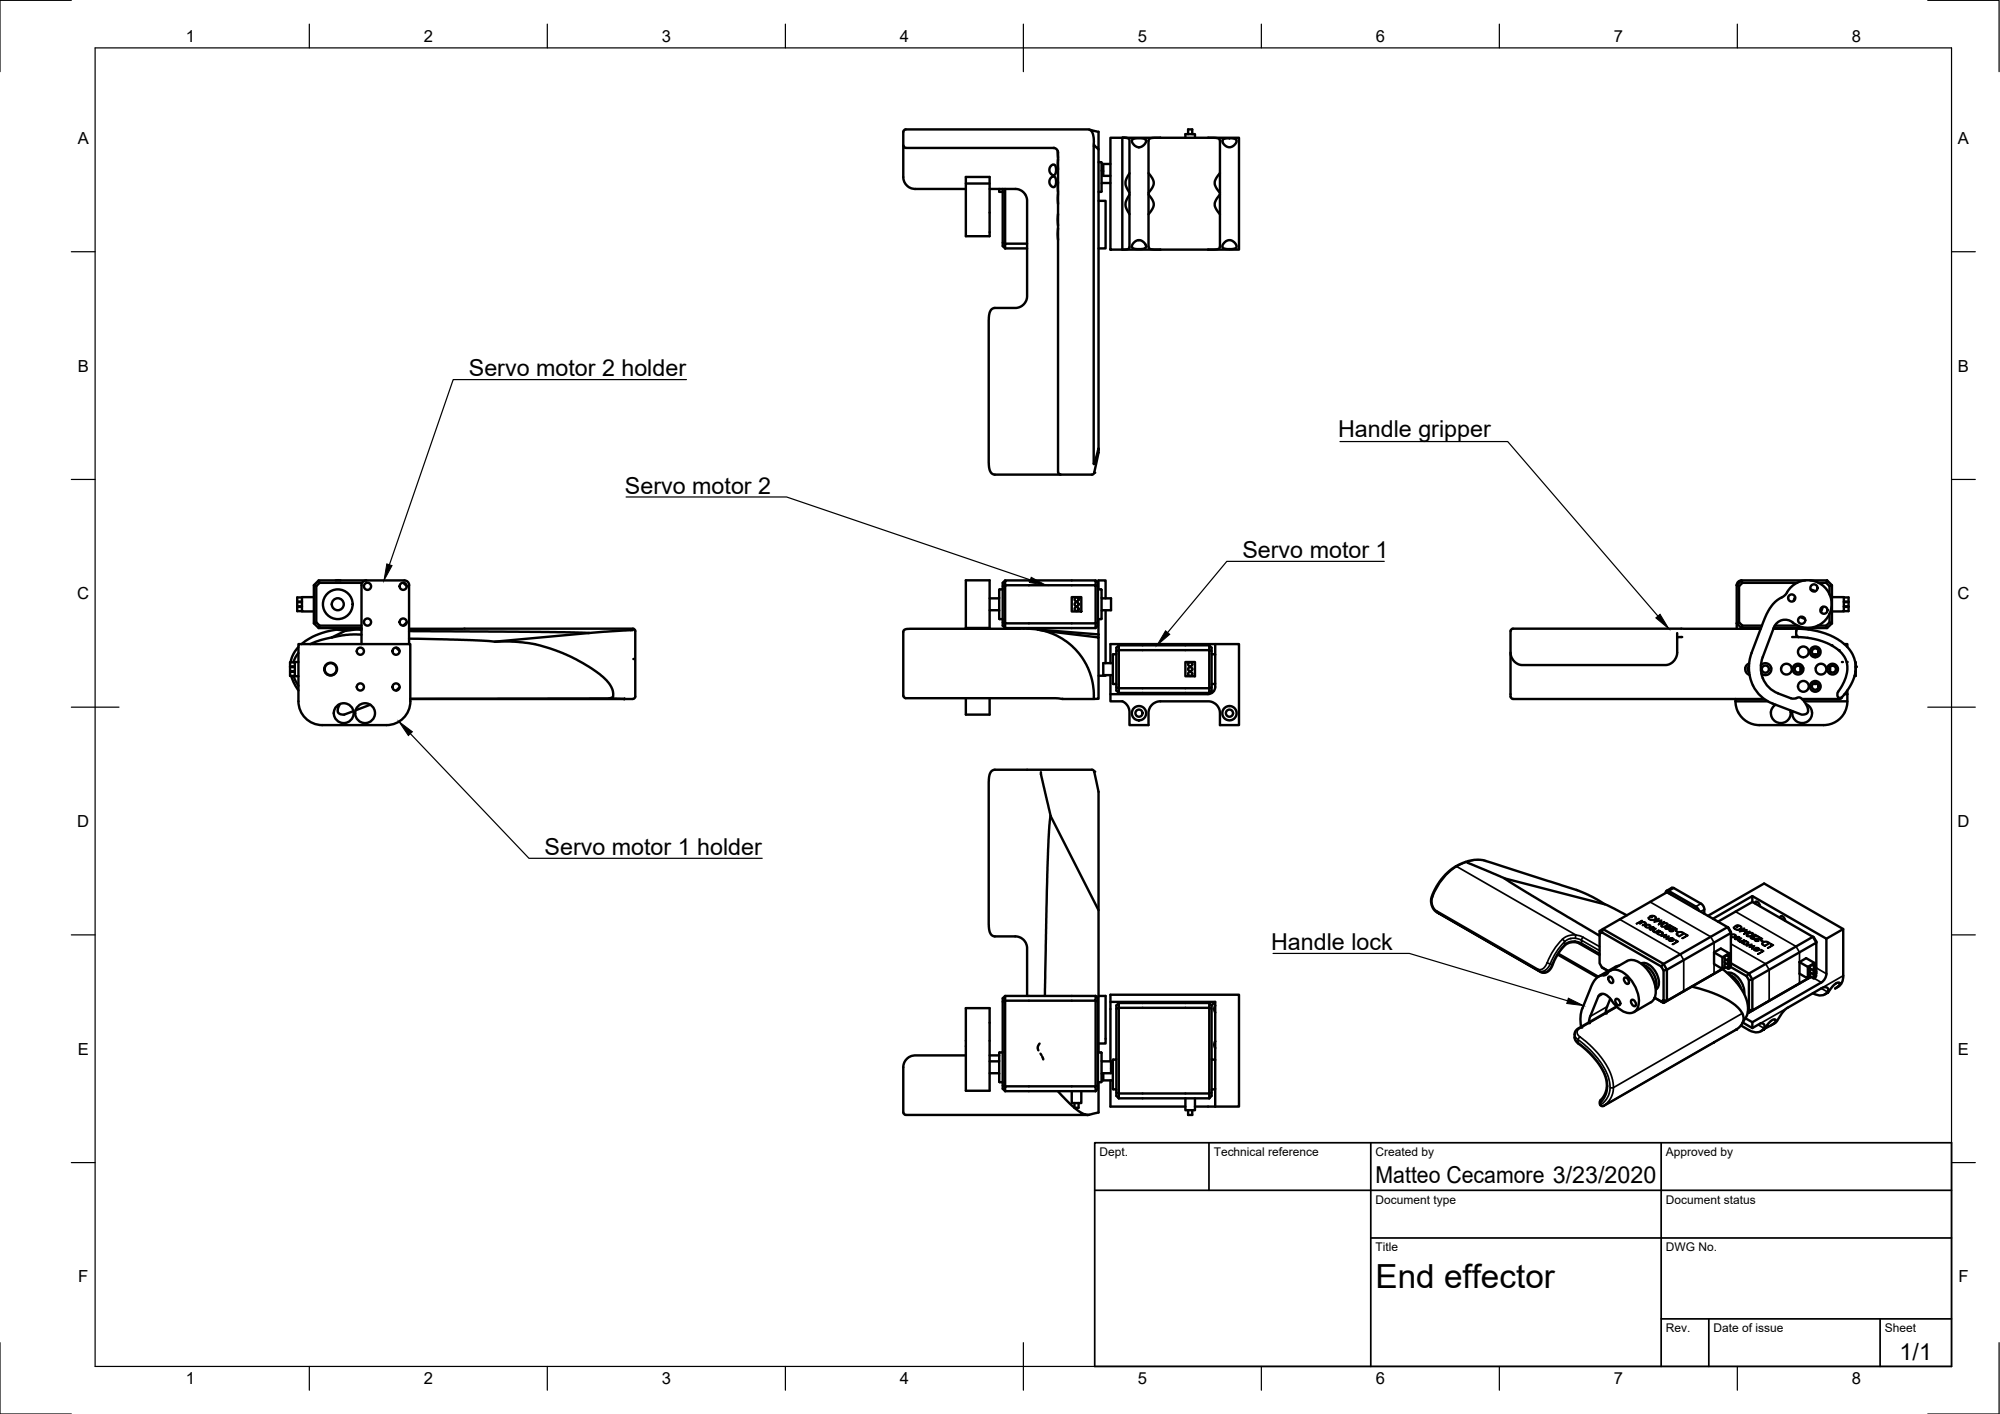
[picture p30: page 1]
Servo motor 2; Servo motor 1; Handle gripper; Handle lock

Servo motor 2 holder

Servo motor 1 holder

Dept. | Technical reference | Created by Matteo Cecamore 3/23/2020 | Approved by

Document type | Document status

Title End effector | DWG No.

Rev. | Date of issue | Sheet 1/1

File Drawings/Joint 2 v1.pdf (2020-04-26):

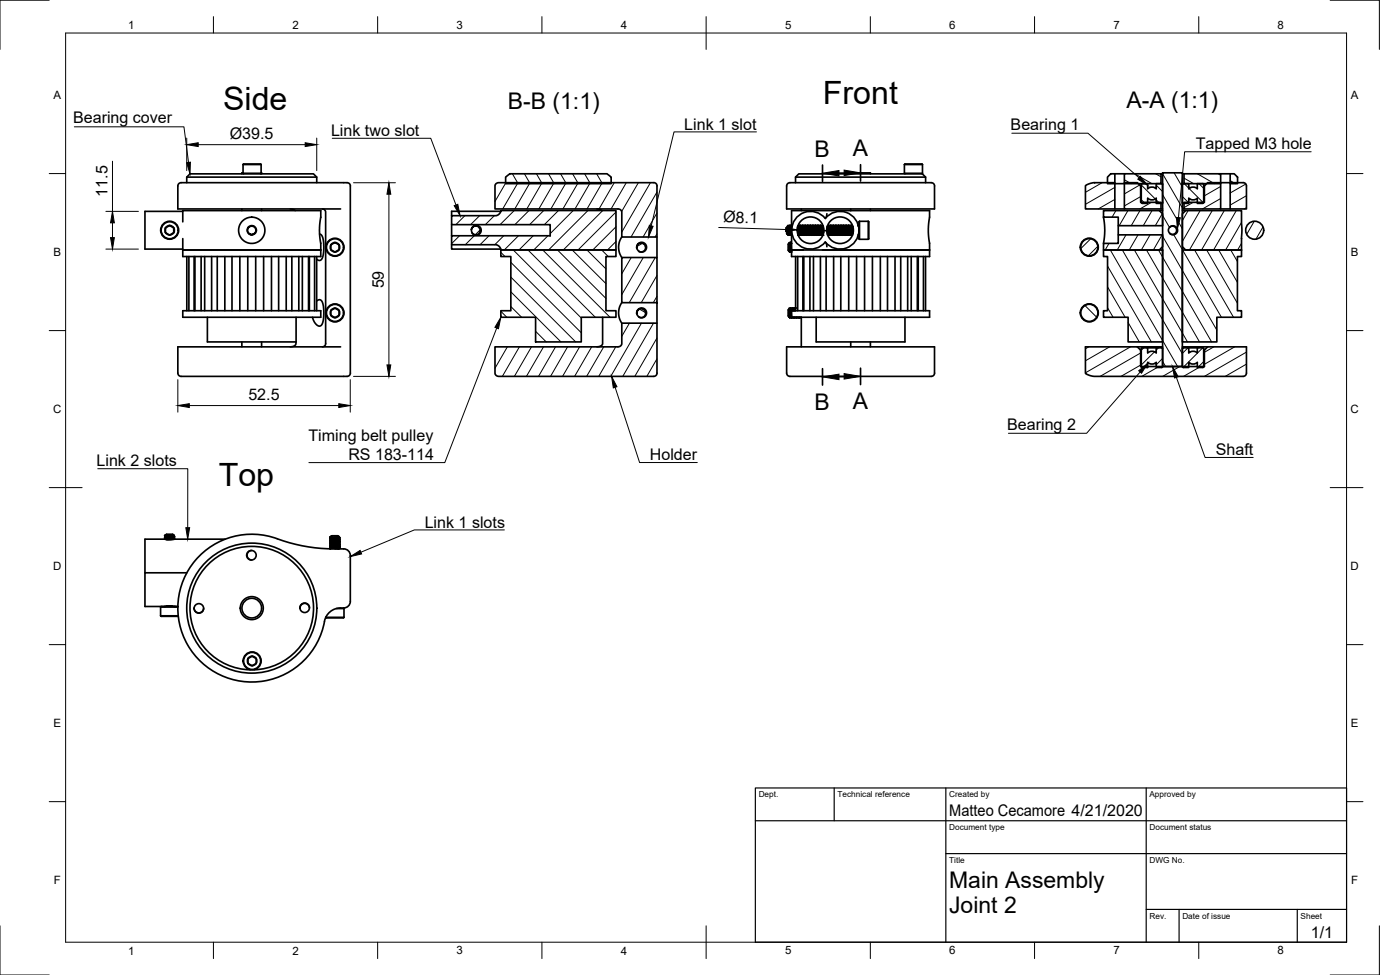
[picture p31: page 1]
Side; Holder; Link two slot; Link 1 slot; Link 2 slots; Bearing 1; Bearing 2; Tapped M3 hole; Shaft 59; Bearing cover Ø39.5 11.5; Link 1 slots

Timing belt pulley

Dept. | Technical reference | Created by Matteo Cecamore 4/21/2020 | Approved by

Document type | Document status

Title Main Assembly Joint 2 | DWG No.

Rev. | Date of issue | Sheet 1/1

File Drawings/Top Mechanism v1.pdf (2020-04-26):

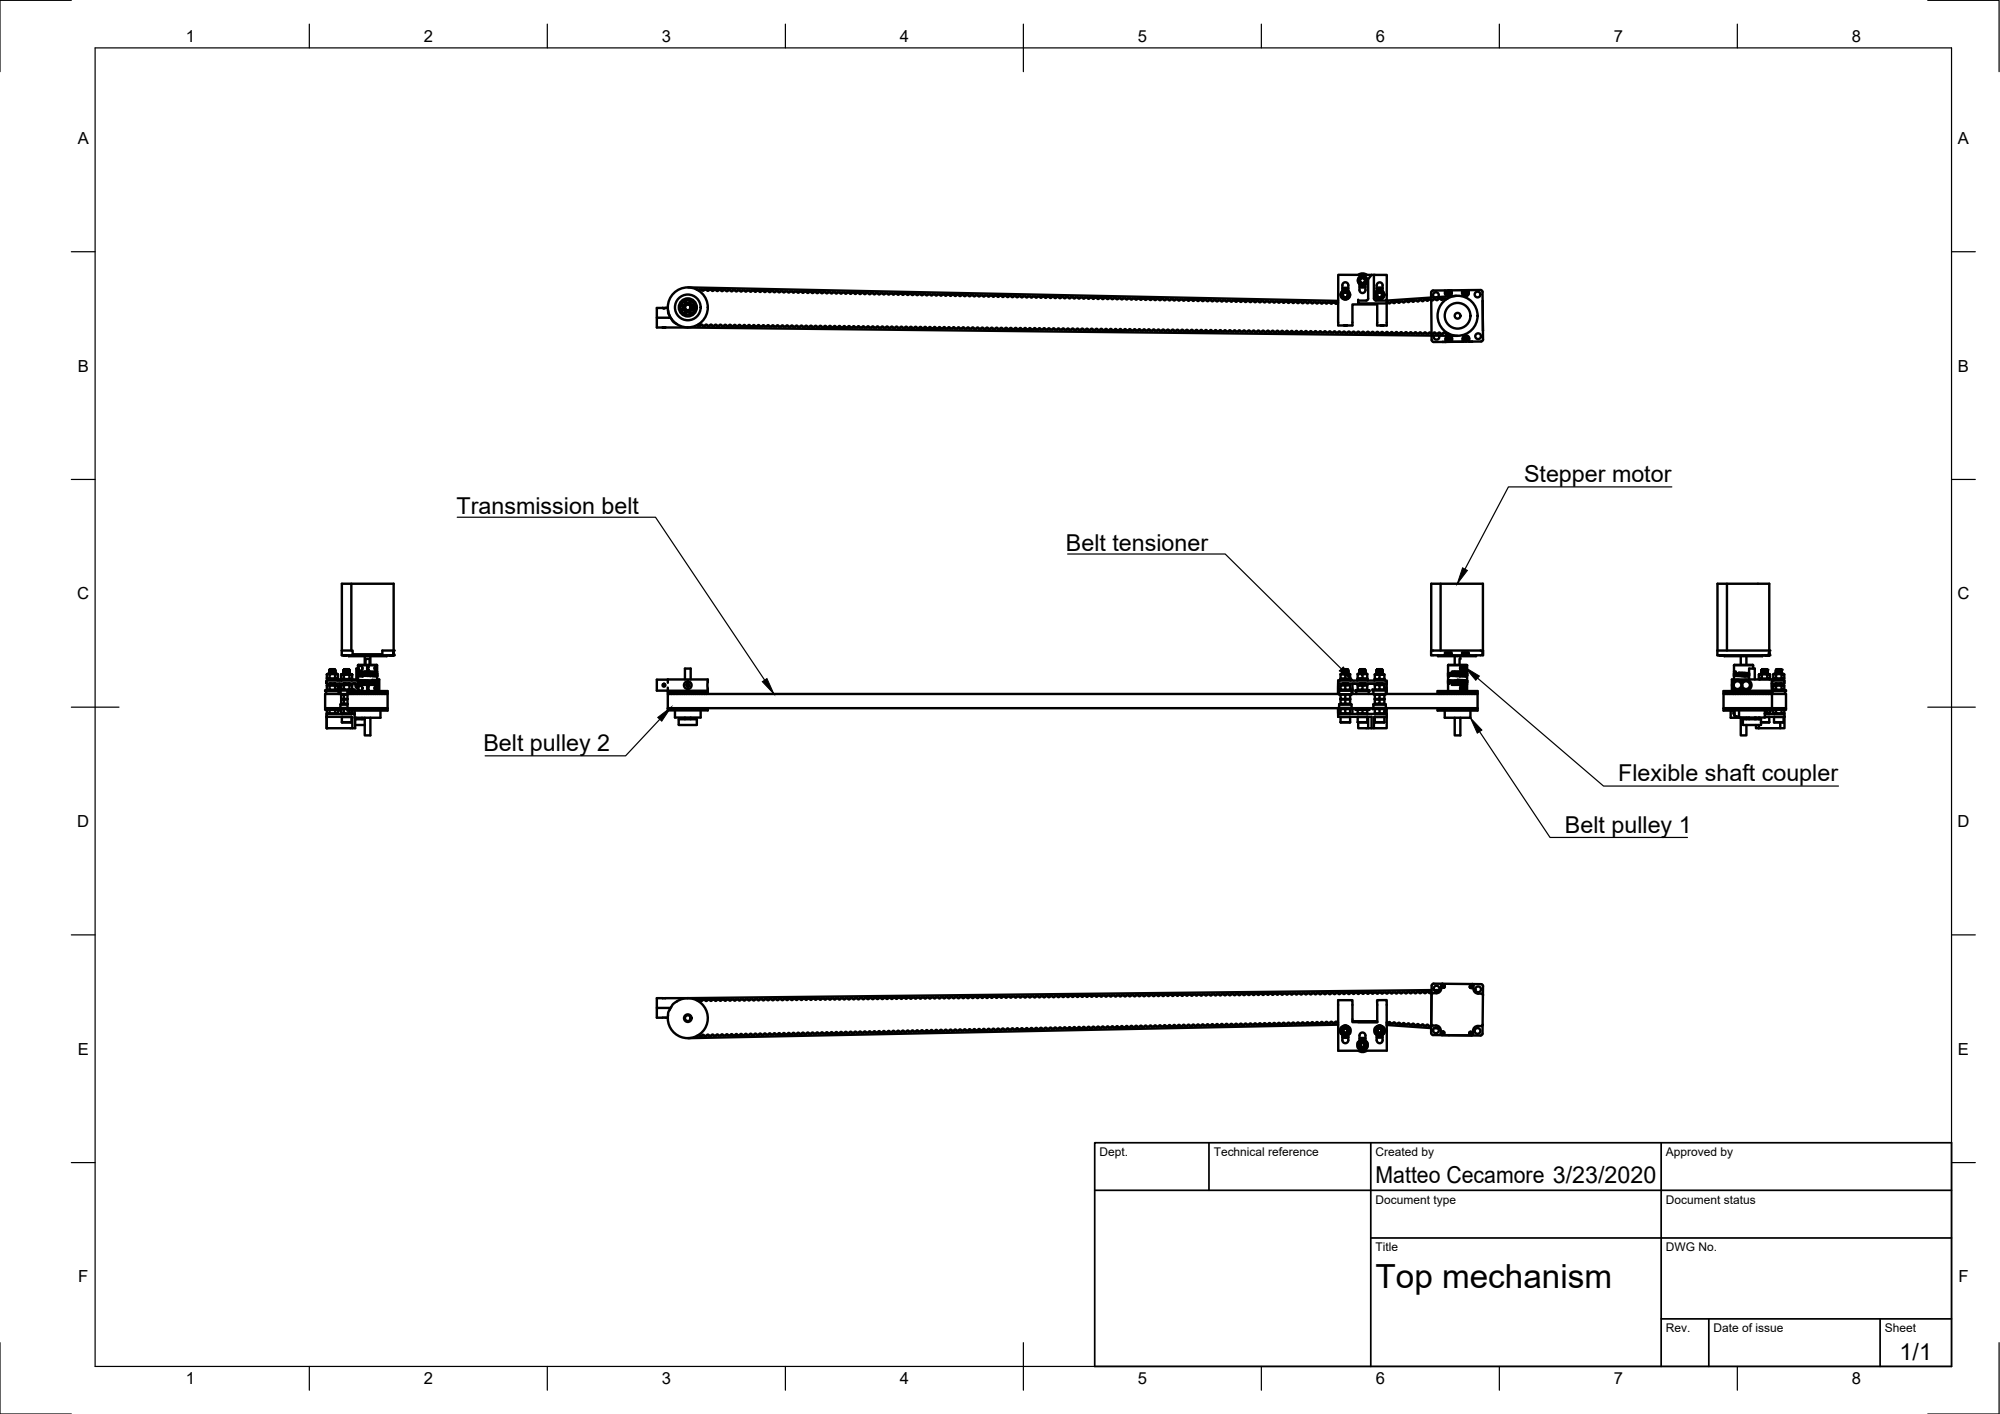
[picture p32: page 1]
Dept.; Technical reference; Created by; Approved by; Document type; Document status; Title; DWG No.; Rev.; Date of issue; Sheet; Top mechanism; Matteo Cecamore; Stepper motor; Belt tensioner; Transmission belt; Belt pulley 1; Belt pulley 2

Flexible shaft coupler

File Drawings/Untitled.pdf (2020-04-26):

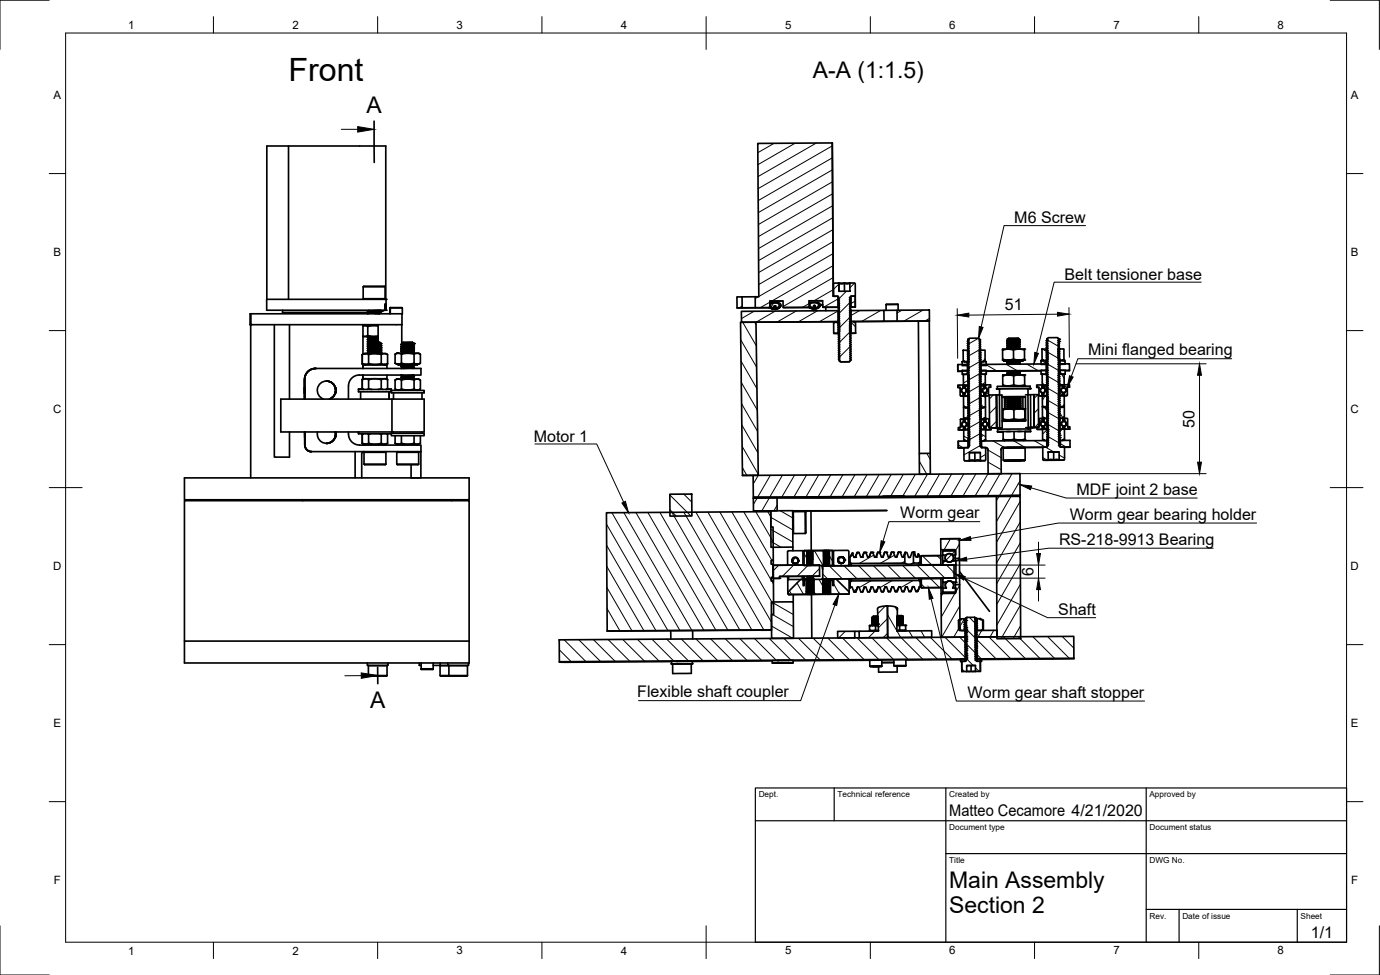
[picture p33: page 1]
M6 Screw; Motor 1; Worm gear

Belt tensioner base

Mini flanged bearing

MDF joint 2 base
Worm gear bearing holder
RS-218-9913 Bearing

Flexible shaft coupler

Worm gear shaft stopper

Dept. | Technical reference | Created by Matteo Cecamore 4/21/2020 | Approved by

Document type | Document status

Title Main Assembly Section 2 | DWG No.

Rev. | Date of issue | Sheet 1/1

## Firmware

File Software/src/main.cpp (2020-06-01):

#include <main.h>

// ========= MOTOR SETUP =========

StepperMotor m1 = (StepperMotor)malloc(sizeof(struct stepper_motor));
StepperMotor m2 = (StepperMotor)malloc(sizeof(struct stepper_motor));

void init_motor1(){
  m1->pulse_plus = M1_PULP;
  m1->pulse_min = M1_PULM;
  m1->dir_plus = M1_DIRP;
  m1->dir_min = M1_DIRM;
  m1->reversed = true;
  m1->currAngle = 0;
  m1->step_mode = FULL_STEP;
  m1->gearing_ratio = 100;

  initMotor(m1);
}

void init_motor2(){
  m2->pulse_plus = M2_PULP;
  m2->pulse_min = M2_PULM;
  m2->dir_plus = M2_DIRP;
  m2->dir_min = M2_DIRM;
  m2->reversed = true;
  m2->gearing_ratio = 1;
  m2->step_mode = THIRTYTWO_STEP;
  m2->currAngle = 0;

  initMotor(m2);
}

// ========= TIMER SETUP =========
//EXTERN C compiles using c compiler not needed for this but needed for cubeMX IRQ_Handler
// timer3.setPrescaleFactor(32000); //Divides maximum clock by the prescaler CLOCK = 64Mhz
// 16-bit up to 65536 period = (clock/prescaler) * time(in seconds)
// TICK_FORMAT = value of the counter
// MICROSEC AND HERTZ doesn't need prescaler
// HERTZ FORMAT cannot take floating point numbers

void timer3_setup(){
  timer3.pause();
  timer3.setMode(1, TIMER_OUTPUT_COMPARE);
  timer3.setOverflow(2000, HERTZ_FORMAT); 
  timer3.attachInterrupt(timer3_handler);
  NVIC_EnableIRQ(TIM3_IRQn); //IT WAS THIS!!!
  // timer3.refresh();
}

void timer2_setup(){
  timer2.pause();
  timer2.setMode(1, TIMER_OUTPUT_COMPARE);
  timer2.setOverflow(2000, HERTZ_FORMAT); 
  timer2.attachInterrupt(timer2_handler);
  NVIC_EnableIRQ(TIM2_IRQn); //IT WAS THIS!!!
  // timer6.refresh();
}

extern "C" void timer3_handler(HardwareTimer *){ 
  //digitalToggle(LED_BUILTIN);
  //digitalToggle(M1_PULM);
  updateMotor(m1);
}

extern "C" void timer2_handler(HardwareTimer *){ 
  // digitalToggle(LED_BUILTIN);
  updateMotor(m2);
}

// ========= TASK 1 : JOYSTICK CONTROL =========

void init_joystick(){
  pinMode(VRx, INPUT);
  pinMode(VRy, INPUT);
  pinMode(BUTTON, INPUT_PULLUP);

  analogReadResolution(12);
}

coordinates joystick_coords = {0,0};
double new_x, new_y, delta_x, delta_y;
coordinates end_effector_coords = {0, MAX_LENGTH - 10};
angles motor_angles = {0, 0};

void joystick_kinematic_task(){

  // Serial.println("Joystick started");

  /*
  * Takes the analog values of the x and y potentiometer on the joystick and converts them in 
  * end effector target x, y positions. The joystick position represents a delta x, y that will
  * be added or subtracted to the current x, y positions.
  */
  joystick_coords.x = end_effector_coords.x;
  joystick_coords.y = end_effector_coords.y;

  new_x = analogRead(VRx);
  new_y = analogRead(VRy);

  delta_x = map(new_x, 0, 4096, -MAX_LENGTH, MAX_LENGTH)/SENSITIVITY;
  delta_y = map(new_y, 0, 4096, MAX_LENGTH, -MAX_LENGTH)/SENSITIVITY; // Joystick has reversed y
  if (new_x > 1900 && new_x < 2100) delta_x = 0;
  if (new_y > 1900 && new_y < 2100) delta_y = 0;
  joystick_coords.x += delta_x;
  joystick_coords.y += delta_y;

  // TODO: Make limits based on workspace.
  if (joystick_coords.x > MAX_LENGTH) joystick_coords.x = MAX_LENGTH;
  if (joystick_coords.x < -MAX_LENGTH) joystick_coords.x = - MAX_LENGTH;
  if (joystick_coords.y > MAX_LENGTH) joystick_coords.y = MAX_LENGTH;
  if (joystick_coords.y < -MAX_LENGTH) joystick_coords.y = - MAX_LENGTH;

  end_effector_coords.x = joystick_coords.x;
  end_effector_coords.y = joystick_coords.y;

  Serial.print("x: "); Serial.print(joystick_coords.x); Serial.print("y: "); Serial.print(joystick_coords.y); 
  Serial.print(" || Vx :"); Serial.print(new_x); Serial.print(" Vy: "); Serial.print(new_y);
  Serial.print(" || M1 :"); Serial.print(m1->currAngle); Serial.print(" M2: "); Serial.print(m2->currAngle);

}

void joystick_joint_task(){

  joystick_coords.x = motor_angles.q1;
  joystick_coords.y = motor_angles.q2;

  new_x = analogRead(VRx);
  new_y = analogRead(VRy);

  delta_x = map(new_x, 0, 4096, -180, 180)/SENSITIVITY;
  delta_y = map(new_y, 0, 4096, 180, -180)/SENSITIVITY; // Joystick has reversed y
  if (new_x > 1900 && new_x < 2100) delta_x = 0; //currPos.inRange()
  if (new_y > 1900 && new_y < 2100) delta_y = 0; //currPos.inRange(optional min, max, axis)

  joystick_coords.x += delta_x;
  joystick_coords.y += delta_y;

  // TODO: Make limits based on workspace.
  if (joystick_coords.x > 180) joystick_coords.x = 180;
  if (joystick_coords.x < -180) joystick_coords.x = -180;
  if (joystick_coords.y > 180) joystick_coords.y = 180;
  if (joystick_coords.y < -180) joystick_coords.y = -180;

  motor_angles.q1 = joystick_coords.x;
  motor_angles.q2 = joystick_coords.y;

  Serial.print("M1: "); Serial.print(joystick_coords.x); Serial.print(" M2: "); Serial.print(joystick_coords.y); 
  Serial.print(" || Vx :"); Serial.print(new_x); Serial.print(" Vy: "); Serial.print(new_y);
  Serial.print(" || M1 :"); Serial.print(m1->currAngle); Serial.print(" M2: "); Serial.println(m2->currAngle);

}

// ========= TASK 2: CALCULATE KINEMATICS =========


void kinematics_task(){ 
  angles targetAngle = inverse_kinematics_planar2R(end_effector_coords);
  Serial.print(" || q1: "); Serial.print((targetAngle.q1)); Serial.print(" q2: "); Serial.println((targetAngle.q2));
  updateTargetAngle(m1, (targetAngle.q1));
  // Serial.println(m1->currAngle);
  updateTargetAngle(m2, (targetAngle.q2));
}

void joint_task(){
  updateTargetAngle(m1, motor_angles.q1);
  updateTargetAngle(m2, motor_angles.q2);
}

// ====== BUTTON =======

int count = 0;
int control_state = CONTROL_JOINTS;

void control_button(int targetState){

  if (digitalRead(BUTTON) == HIGH) {
    count = 0;
    return;
  } 

  Serial.print("BUTTON PRESSED");
  count++;
  if (count == 12){
    Serial.print("STATE CHANGED");
    count = 0;
    control_state = targetState;

    if (control_state == CONTROL_KINEMATICS){

      Serial.print("GOING TO KINEMATICS CONTROL");

      end_effector_coords = forward_kinematics_planar2R(motor_angles);

    } else if(control_state == CONTROL_JOINTS){
      Serial.print("GOING TO JOINT CONTROL");

      motor_angles = inverse_kinematics_planar2R(end_effector_coords);

      
    }
  }
}

// ========= MAIN =========
void setup(){
  Serial.begin(9600);

  // pinMode(LED_BUILTIN, OUTPUT);
  timer3_setup();
  timer2_setup();
  init_motor1();
  init_motor2();
  init_joystick();

  // Resume timers after motor setup
  timer3.resume();
  timer2.resume();

}

// void joystick_task2(){

//   /*
//   * Takes the analog values of the x and y potentiometer on the joystick and converts them in 
//   * end effector target x, y positions. The joystick position represents a delta x, y that will
//   * be added or subtracted to the current x, y positions.
//   */

//   //Serial.println("Joystick started");

//   new_x = analogRead(VRx);
//   delta_x = map(new_x, 0, 4096, -360, 360)/SENSITIVITY;
//   if (new_x > 1900 && new_x < 2100) delta_x = 0;
//   x += delta_x;

//   // TODO: Make limits based on workspace.
//   if (x > 360) x = 360;
//   if (x < -360) x = -360;

//   Serial.print("x: "); Serial.print(x); 
//   Serial.print(" || Vx :"); Serial.print(analogRead(VRx));
// }

void loop(){

  switch (control_state)
  {
  case CONTROL_KINEMATICS:

    control_button(CONTROL_JOINTS);
    joystick_kinematic_task();
    kinematics_task();
    
    break;

  case CONTROL_JOINTS:

    control_button(CONTROL_KINEMATICS);
    joystick_joint_task();
    joint_task();
    break;
  
  }

  delay(100);

}

  // #ifdef CCW
  // // DIR: HIGH - LOW = CW
  // // DIR: LOW - HIGH = CCW
  // digitalWrite(M1_DIRM, HIGH);

  // #else

  // digitalWrite(M1_DIRM, LOW);

  // #endif

  // // M1 IS REVERSED
  // //digitalWrite(M2_PULP, HIGH);
  // //digitalWrite(M2_PULM, LOW);

  // // DIR: HIGH - LOW = CCW
  // #ifdef CCW
  // digitalWrite(M2_DIRM, LOW);
  // #endif
  // // DIR: LOW - HIGH = CW
  // #ifdef CW
  // digitalWrite(M2_DIRM, HIGH);
  // #endif

// extern "C" void timer_setup(){
//   RCC->APB1ENR |= 0x00000002;
//   TIM3->PSC = 320000;         // Set prescaler to 24 000 (PSC + 1)
//   TIM3->ARR = 65500;           // Auto reload value 1000
//   TIM3->DIER = TIM_DIER_UIE; // Enable update interrupt (timer level)
//   TIM3->CR1 = 0x0001;   //enable timer
//   NVIC->ISER[0] |= 0x20000000;

// }

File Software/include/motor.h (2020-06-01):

#ifndef MOTOR_H
#define MOTOR_H
#include <Arduino.h>
#include <kinematics.h>
#include <math.h>

#define CW 1
#define CCW 0
#define PULSE 0
#define NO_PULSE 1
#define ANGLE_PER_FULL_STEP 1.8
#define FULL_STEP 1
#define HALF_STEP 2
#define QUARTER_STEP 4
#define THIRTYTWO_STEP 32
#define GEAR_MULTIPLIER 100

struct stepper_motor{

    int pulse_plus;
    int pulse_min;
    int dir_plus;
    int dir_min;

    // Gearing ratio 1 if 1:1 ratio, 100 id 100:1 output
    // allows the angle to be controlled based on the output gear

    int gearing_ratio;

    // If the motor is upside down the clockwise direction is opposite
    bool reversed;

    // Set the appropriate pin values for CW or CCW depending on the motor
    int cw;
    int ccw;

    // Current direction of motor
    int dir;

    // Stepper motor step mode
    int step_mode;

    // Variables that are modified in the timer handlers
    uint16_t steps; //360/(1.8/stepMode)
    double currAngle;

};

// Motor identified by its pointer so that we are passing it to the function 
// by reference and modifying it in place without having to return it, we can have it global
typedef struct stepper_motor * StepperMotor; 

void initMotor(StepperMotor m);

// Angle can be positive or negative in degrees, direction is calculated accordingly
void updateTargetAngle(StepperMotor m, double targetAngle);

// runs repeatedly to move the motor to its goal
void updateMotor(StepperMotor m);
void pulseMotor(StepperMotor m);

void stopMotor(StepperMotor m);

// setup externally defined variables
// StepperMotor m1;
// StepperMotor m2;

#endif

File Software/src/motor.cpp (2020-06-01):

#include <motor.h>

void initMotor(StepperMotor m){
    pinMode(m->pulse_plus, OUTPUT);
    pinMode(m->pulse_min, OUTPUT);
    pinMode(m->dir_plus, OUTPUT);
    pinMode(m->dir_min, OUTPUT);

    digitalWrite(m->pulse_plus, HIGH);
    digitalWrite(m->dir_plus, HIGH);

    if(m->reversed){
        m->cw = CCW;
        m->ccw = CW;
    } else {
        m->cw = CW;
        m->ccw = CCW;
    }

    m->steps = 0;
    m->dir = m->cw;
}

int reverse_dir(int dir){
    if(dir == CW) dir = CCW;
    if(dir == CCW) dir = CW;
    return dir;
}

void updateTargetAngle(StepperMotor m, double targetAngle){

    // always take the shorter route between current and target angle
    //Angles between 0 and 360 in radians

    // Give a 2 degree space to allow for double imprecision motor.inRange(1)

    if(targetAngle - 1 <  m->currAngle && m->currAngle < targetAngle + 1){
        return;
    }

    // Determine direction
    // Positive angle direction is CCW from 0 to 360 
    
    if (targetAngle >= m->currAngle) {
        m->dir = m->cw;
        // Serial.print("CW");
    } else {
        m->dir = m->ccw;
        // Serial.print("CCW");
    }   
        
    if (targetAngle <= -360) targetAngle = -360;

    if (targetAngle >= 360) targetAngle = fmod(targetAngle, 360);

    //Serial.print(" TargetAngle: "); Serial.print(targetAngle);

    float angleDifference = m->currAngle - targetAngle;

    // Load the difference in angles converted to steps dicretize it by casting to int
    m->steps = (uint16_t)(((abs(angleDifference))
                                    /
                                (ANGLE_PER_FULL_STEP
                                        /
                                (m->step_mode)))                            *2*(m->gearing_ratio));
    //Serial.print("AngleDifference: "); Serial.print(targetAngle); Serial.print(" Current angle: "); Serial.print(m->currAngle); Serial.print(" Steps"); Serial.println(m->steps);
    // Serial.print(" STEPS: "); Serial.print(m->steps);

    // HIGH = 1 CW = 1
    // LOW = 0 CCW = 0
    // set direction

    // if(m->reversed){
    //     m->dir = reverse_dir(m->dir);
    // }
    
    digitalWrite(m->dir_min, m->dir);  
        

}

void updateMotor(StepperMotor m){

    if (m->steps > 0){ // if steps still havent been finished yet
    
        (m->steps)--;

            //Serial.println(m->steps);
            if(m->dir == m->cw){ // update current position values
                if (m->currAngle >= 360) m->currAngle = fmod(m->currAngle, 360);
                m->currAngle += (0.9)/((m->step_mode)*(m->gearing_ratio)); // update the current position remove the corresponding angle per step
            } else {
                if(m->currAngle <= -360) m->currAngle = -360;
                m->currAngle -=  (0.9)/((m->step_mode)*(m->gearing_ratio)); // 1.8 degrees in radians/step 0.0314159
            }
       
        digitalToggle(m->pulse_min);
    }
}

void stopMotor(StepperMotor m){
    m->steps = 0;
}
